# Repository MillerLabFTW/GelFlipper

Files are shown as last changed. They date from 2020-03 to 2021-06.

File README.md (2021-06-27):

# GelFlipper
#### Open-source gel flipper design for seeding endothelial cells
#### Miller Lab: Physiologic Systems Engineering and Advanced Materials
#### [millerlab.rice.edu](http://millerlab.rice.edu)
#### Project designed by Ian Kinstlinger; revised 04/2020

This repo provides fabrication files, Arduino code, and circuit schematics for our open-source gel flipping system for seeding endothelial cells into patterned vascular networks. See our [Nature Protocols paper](https://rdcu.be/clcY7) (specifically Box 1) for more info.

**Update 06/21:** We now provide blueprints and assembly instructions for our v2 flipper design, which is designed to replace the v1 hardware. Instead of interlocking gears, we use a single rotating block which holds multiple perfusion chambers. Up to 10 at a time are possible with our current design, which can be modified further. 

In our hands, this new version is more reliable because it eliminates occasional issues with the gears jamming during flipping. The main downside is that large gels cannot be flipped in large batches, and there is less flexibilty to swap in and out different gears.

**How to cite:** If you use this device for work in a publication, please cite this project as

Kinstlinger, I.S., Calderon, G.A., Royse, M.K. et al. Perfusion and endothelialization of engineered tissues with patterned vascular networks. Nat Protoc (2021). https://doi.org/10.1038/s41596-021-00533-1

**Questions:** Inquiries about this hardware, issues with assembly or operation, and feature requests can be directed to ian [dot] kinstlinger [at] gmail [dot] com.

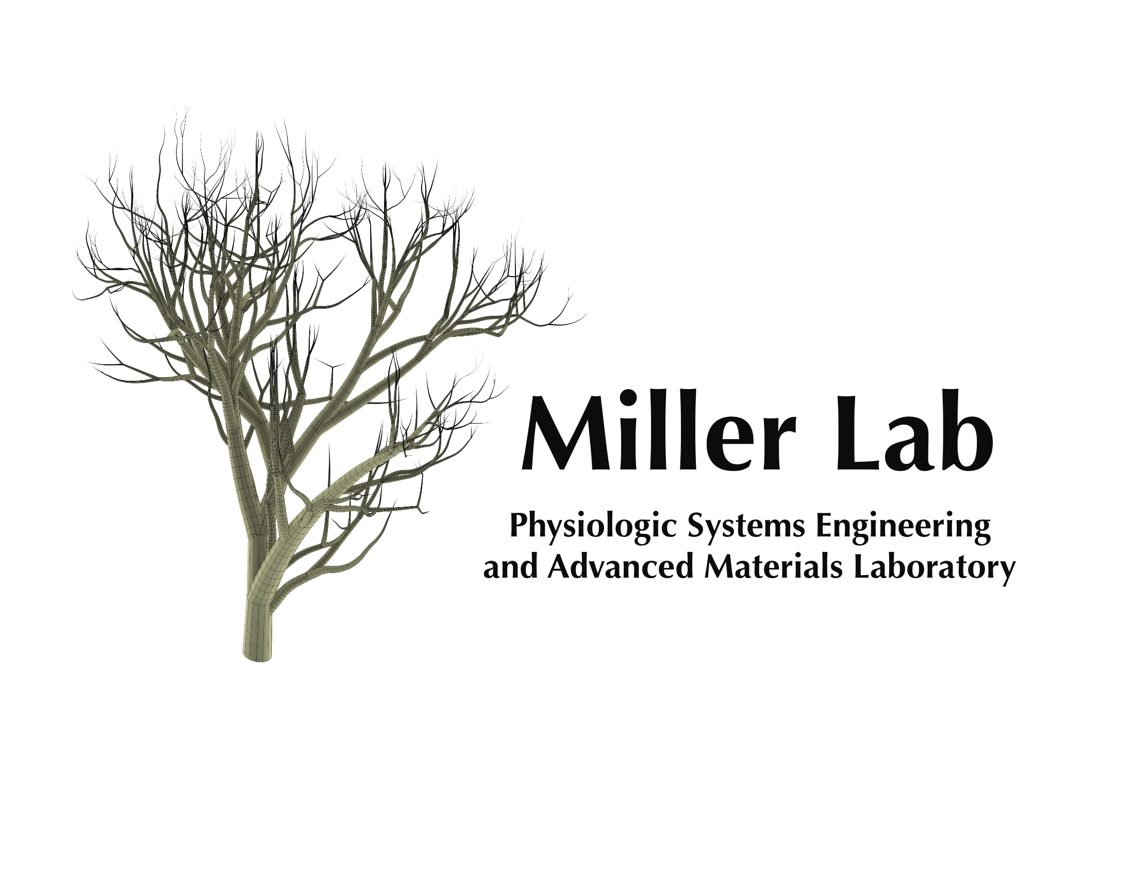
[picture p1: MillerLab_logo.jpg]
MillerLab logo


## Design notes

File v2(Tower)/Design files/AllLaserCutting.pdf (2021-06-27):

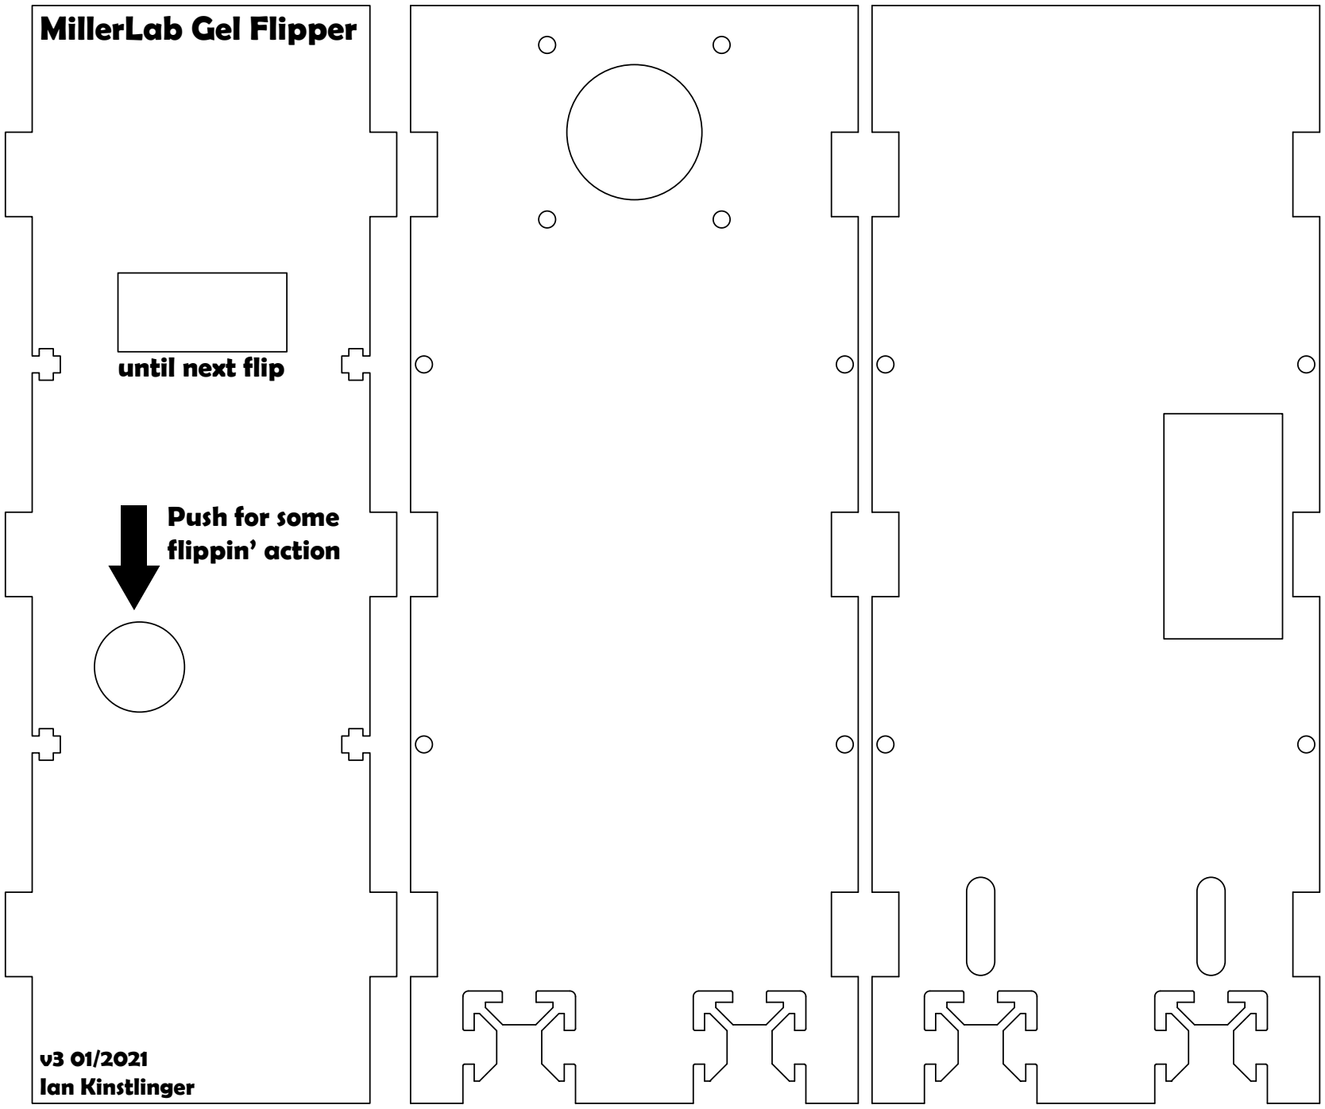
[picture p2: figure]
MillerLab Gel Flipper; until next flip; Push for some flippin’ action; v3 01/2021 Ian Kinstlinger

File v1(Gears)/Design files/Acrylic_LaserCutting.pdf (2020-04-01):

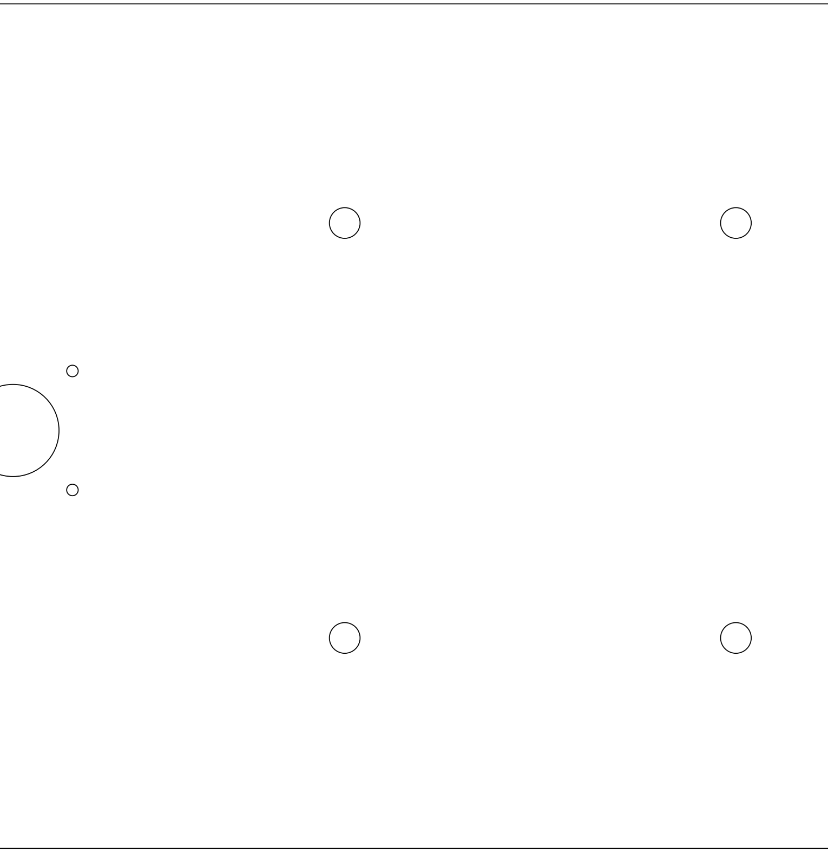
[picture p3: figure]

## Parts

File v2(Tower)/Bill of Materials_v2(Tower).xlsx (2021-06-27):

 | Perfusion chamber BOM
 | Part | Vendor | Part Number | Quantity | Notes
Electronics | Arduino Nano (or equivalent) | Amazon | Amazon link (https://www.amazon.com/Arduino-A000005-ARDUINO-Nano/dp/B0097AU5OU?ac_md=2-0-VW5kZXIgJDI1-ac_d_pm&cv_ct_cx=arduino+nano) | 1 | For all electronics items, there are many excellent vendors and suitable equivalent parts. This BOM is for a protoboard-based controller design, which requires permanently soldering the components to the board and to one another. An equivalent controller can be built on a breadboard, but we highly recommend the protoboard for making it permanent.
 | Protoboard | Amazon | Amazon link (https://www.amazon.com/Prototype-Universal-Protoboard-Soldering-Compatible/dp/B07W83VJGV?s=electronics) | 1
 | Pololu A4988 stepper motor driver | Pololu | 1182 | 1
 | NEMA 17 stepper motor | Adafruit | 324 | 1
 | LED pushbutton | Adafruit | 915 | 1
 | 2.1mm DC barrel jack for protoboard | Adafruit | 373 | 1
 | TM1637 4 digit 7-segment display | Amazon | Amazon link (https://www.amazon.com/OctagonStar-Digital-Display-Module-Arduino/dp/B01M16X6MB) | 1
 | Connector wires with 4-pin headers | Amazon | Amazon link (https://www.amazon.com/2-54mm-Breadboard-Testing-Jumper-Colorful/dp/B00O9Y3LGS) | 2
 | Breakaway headers | Adafruit | 400 | 1
 | Solid-core wire | Adafruit | 290 | 1
 | 12V DC power supply w/ barrel end | Adafruit | 352 | 1
Hardware | 3D printing filament (PLA or equivalent) | Ultimachine |  |  | Or your favorite filament vendor
 | Acrylic sheet, 12 x 24 x 0.375 in. (3/8" thick) | McMaster-Carr | 8589K61 | 1 | Many good vendors for acrylic sheets. We used 3/16" for this design
 | M3 x 10 screws | McMaster-Carr | 91292A113 | 1 pk of 100
 | M3 nuts | McMaster-Carr | 90591A250 | 1 pk of 100
 | M3 washers | McMaster-Carr | 93475A210 | 1 pk of 100
 | 20x20 mm aluminum T-slot extrusion | McMaster-Carr | 5537T911 | 2x ~12 inch pieces | Aluminum extrusions act as feet to stabilize the device; the exact length is not critical. If you have extrusion on hand, you can cut to length as needed with a hacksaw
 | Aluminum extrusion corner bracket | McMaster-Carr | 5537T81 | 2
 | Fastener nut for aluminum extrusion | McMaster-Carr | 5537T75 | 2
 | M5 x 12 screw | McMaster-Carr | 91274A127 | 1 (50 pack) | These nuts and bolts are to secure the aluminum extrusion -- the length of screw you need may depend on acrylic thickness and type of corner brackets used.
 | M5 nut | McMaster-Carr | 90592A095 | 1 (100 pack)
 | Fastener nut for aluminum extrusion | McMaster-Carr | 5537T75 | 2
 | (suggested) Acrylic glue; e.g. Weld-On SciGrip #4 | McMaster-Carr | 7517A1 | 1

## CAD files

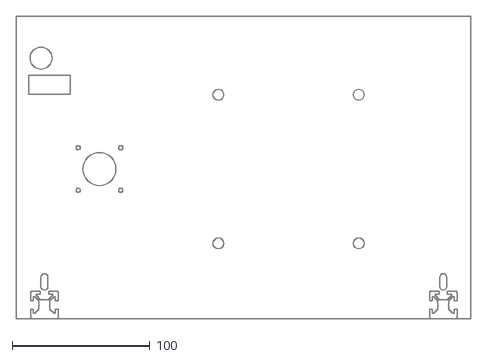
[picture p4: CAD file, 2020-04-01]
v1(Gears)/Design files/Acrylic_LaserCutting.dxf
330.5 x 220.0

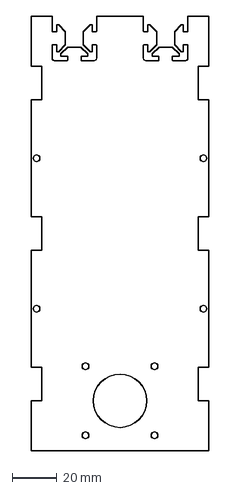
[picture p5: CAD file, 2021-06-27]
v2(Tower)/Design files/MotorSide.dxf
79.5 x 195.0 mm

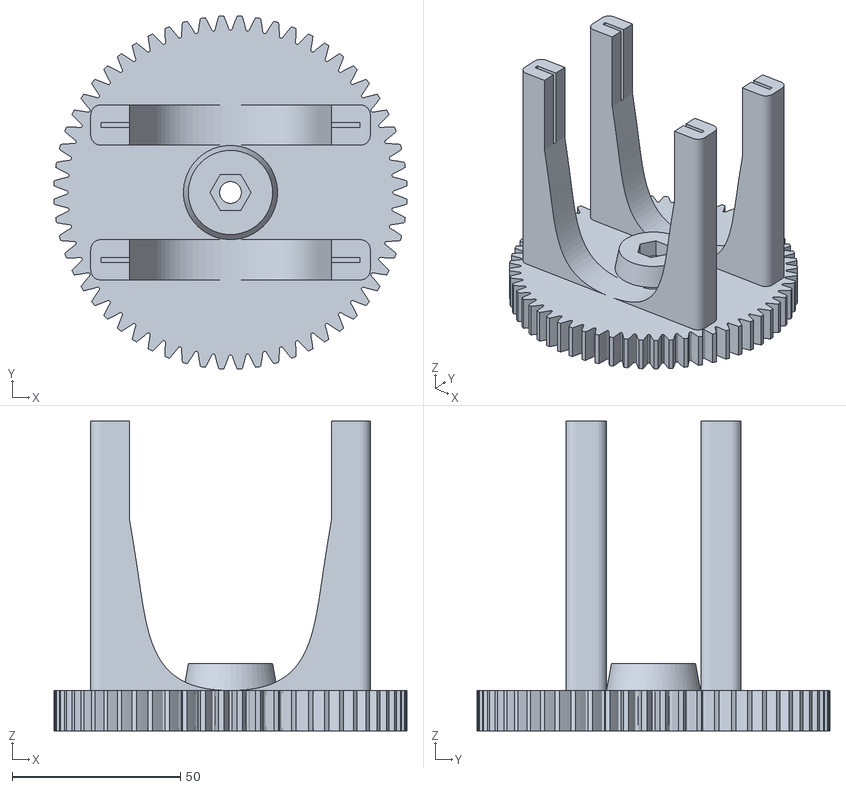
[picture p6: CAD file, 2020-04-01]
v1(Gears)/Design files/FlipGearv3.stl
104.8 x 104.8 x 92.0

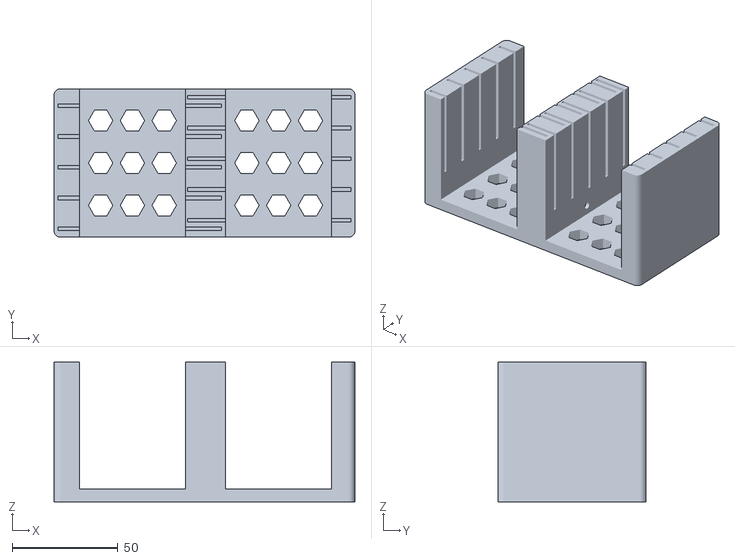
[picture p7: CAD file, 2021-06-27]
v2(Tower)/Design files/PerfChamberHolder.stl
142.0 x 70.0 x 66.0

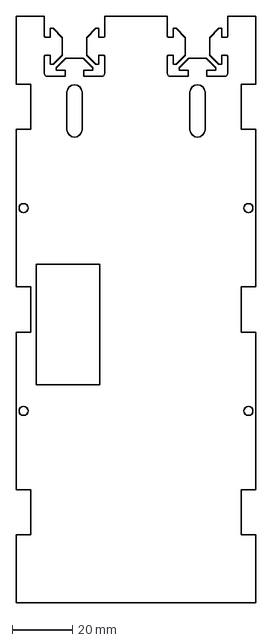
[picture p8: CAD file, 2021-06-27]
v2(Tower)/Design files/PlugSide.dxf
79.5 x 195.0 mm

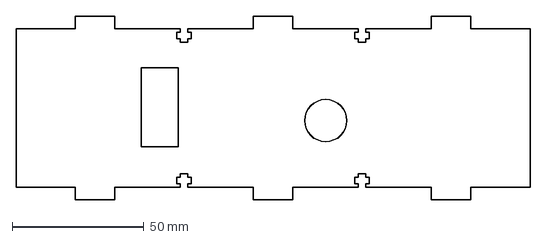
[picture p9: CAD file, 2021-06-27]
v2(Tower)/Design files/TimerSide.dxf
195.0 x 69.5 mm

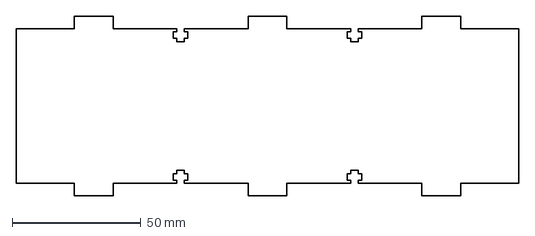
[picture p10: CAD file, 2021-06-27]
v2(Tower)/Design files/ControllerSide.dxf
195.0 x 69.5 mm

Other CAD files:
v1(Gears)/Design files/FlipGearMotorv3.stl
v2(Tower)/Design files/PerfChamberHolder.f3d

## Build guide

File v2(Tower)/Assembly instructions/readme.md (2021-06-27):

### Assembly instructions for gel flipper hardware -- tower version

### See BOM for parts list needed for this build

### 1. Fabricate laser-cut acrylic sheet and 3D print gears
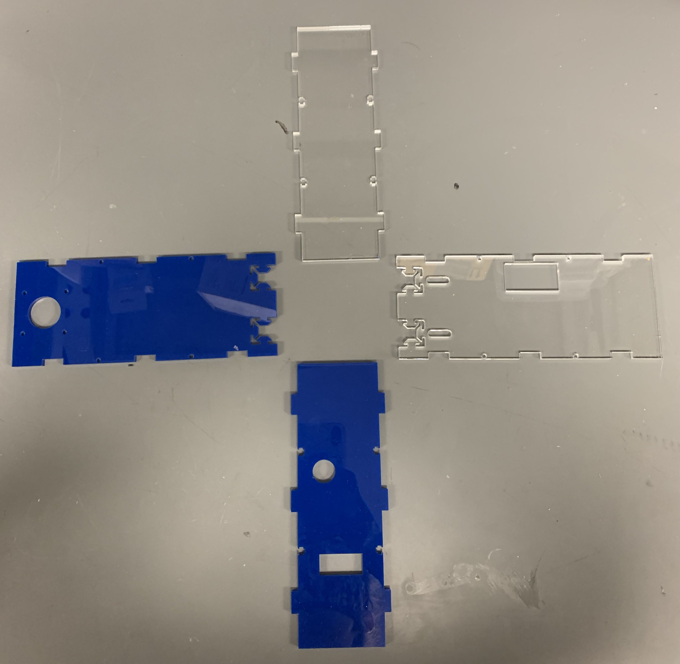
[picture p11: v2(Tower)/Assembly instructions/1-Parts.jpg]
Fabricate parts


Laser cutting: Adjust DXF file as needed. Interlocking tabs should change size if you use acrylic of thickness other than 3/16". Text is added in the Illustrator and PDF files. Fun color and customizations are encouraged!
3D printing: Print the chamber-holding piece which slides onto the motor shaft (not shown here). 

### 2. Assemble first two walls
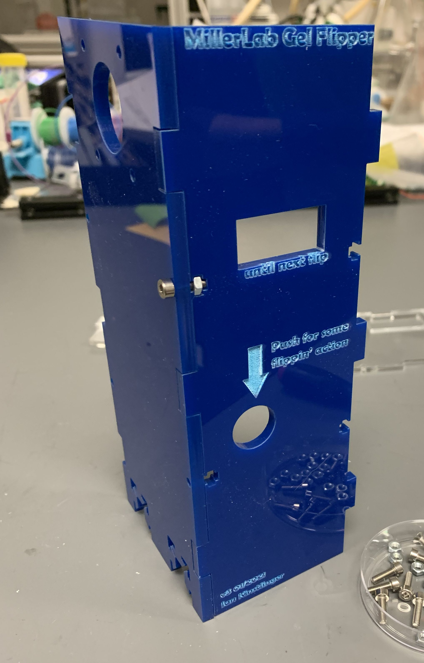
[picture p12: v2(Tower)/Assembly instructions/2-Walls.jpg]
Build walls


Use M3-10mm bolts and M3 nuts to secure the motor-side wall to the button-side wall. Nuts slide into the traps from the side. Carefully tighten until the pieces don't wiggle, but don't overtighten or the acrylic can crack.

### 3. Attach NEMA 17 motor
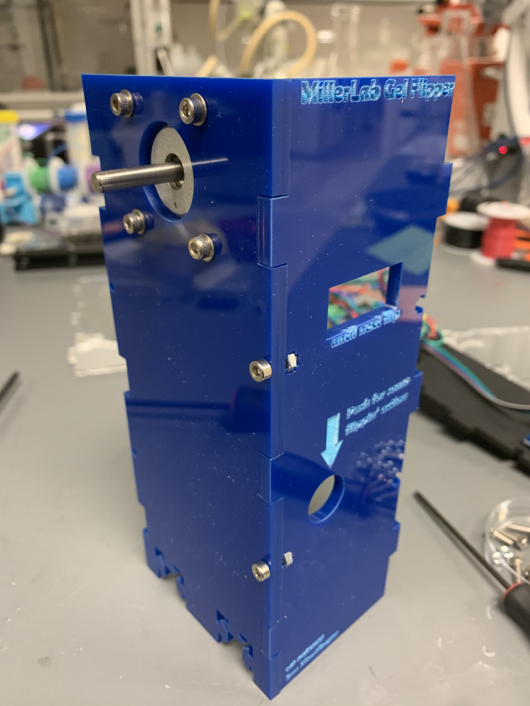
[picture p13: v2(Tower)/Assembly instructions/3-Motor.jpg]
Attach motor


Use M3 hex bolts and washers.

### 4. Mount button and time display
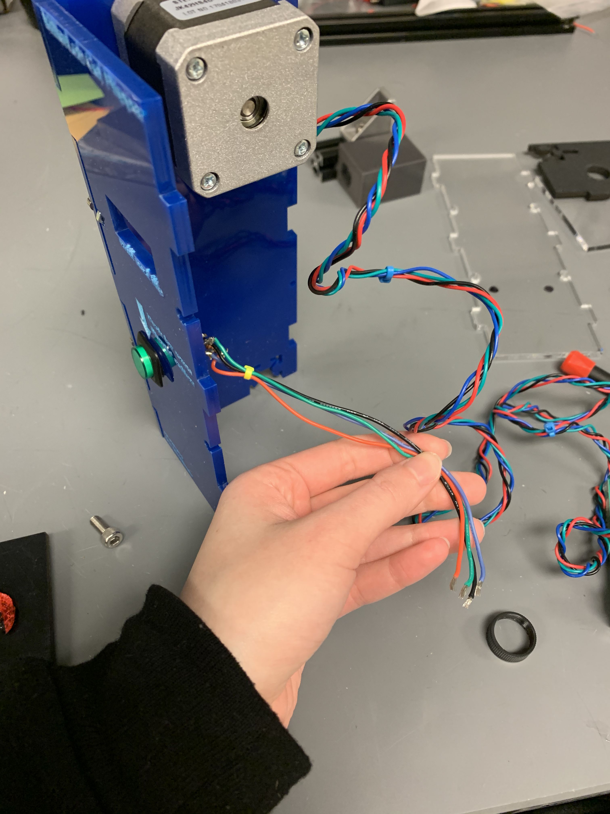
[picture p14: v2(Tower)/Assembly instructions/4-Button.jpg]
Mount motor gear


Install the 7 segment display and start/stop button into the laser-cut slots. If the display is not snug against the acrylic, it can be hot glued or taped from the back.

### 5. Mount controller onto acrylic wall
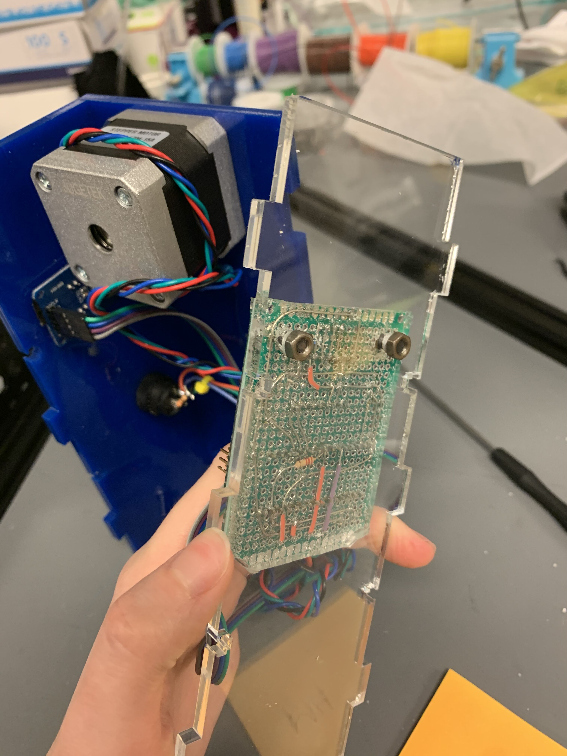
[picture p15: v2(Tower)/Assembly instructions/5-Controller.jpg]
Mount controller


Use nuts and bolts to attach the Arduino controller to the acrylic piece shown. Here, we drilled 4mm holes in the acrylic and the protoboard. You can also add these holes to the original laser cutting file. It doesn't matter what diameter bolts are used, but we used M4 here. Note that we also encased the controller circuit in PDMS (Sylgard 184) to protect it from degradation in the incubator.

### 6. Join controller wall with other walls
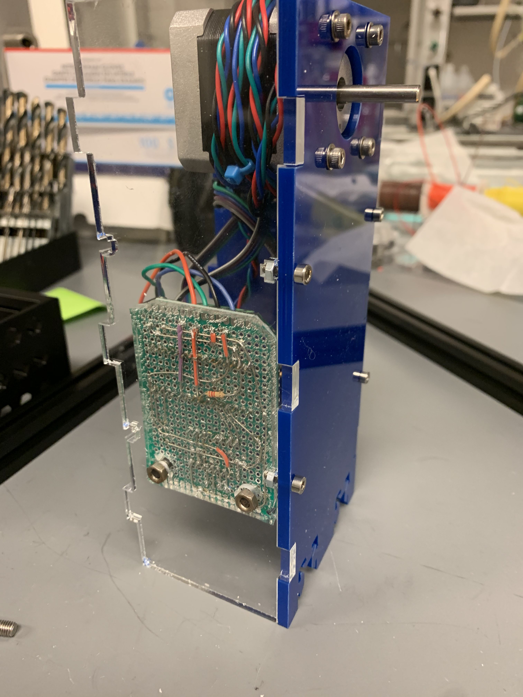
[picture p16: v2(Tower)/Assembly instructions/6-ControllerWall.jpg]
Join walls


Use more M3-10mm bolts and nuts to add the third wall to the first two. At this stage, we suggest using acrylic glue to semi-permanently hold together these 3 walls. Use caution when handling the glue; wear gloves and safety glasses and work in a well-ventilated workspace.

At this point, if not already connected, plug the start button and timer display into the controller. 

### 7. Mount aluminum T-slot legs onto final wall
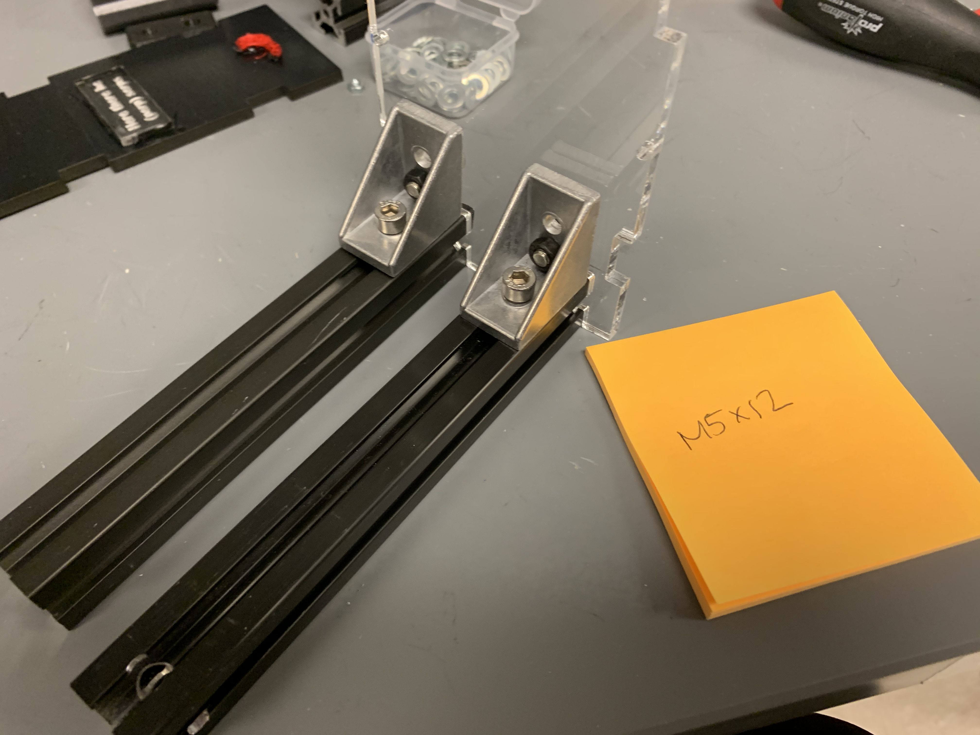
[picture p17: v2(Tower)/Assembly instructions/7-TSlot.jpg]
Mount T-slot


We use T-Slot extrusion as a stable base for the flipper so that when gels are flipped, their added weight doesn't topple the tower. It can be cut to size with a hacksaw, and the exact length is not critical as long as the tower is stable.

Here we use M5 nuts and brackets to secure the T-slot; other mounting hardware is possible too.

### 8. Assemble final  wall
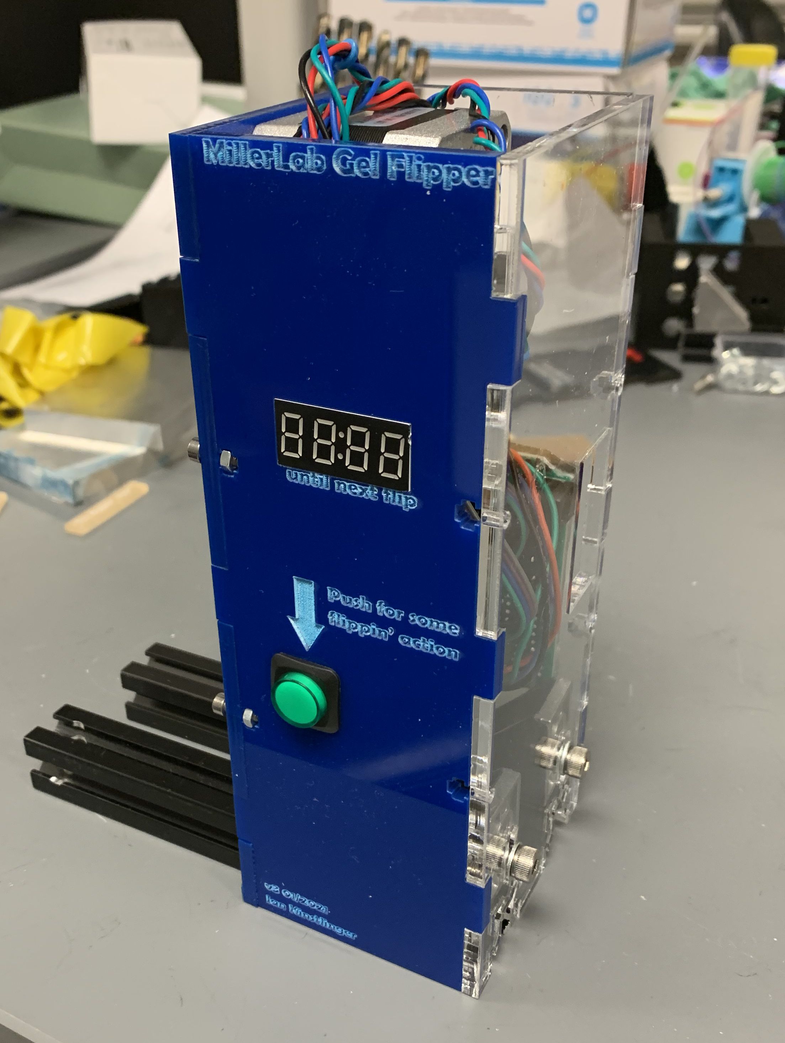
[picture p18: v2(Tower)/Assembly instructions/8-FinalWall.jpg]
Final wall


Feed the free end of the aluminum extrusion through the slots in the motor-side wall until the final wall slots into place. Use M3-10mm bolts to secure.

### 9. Add chamber holder
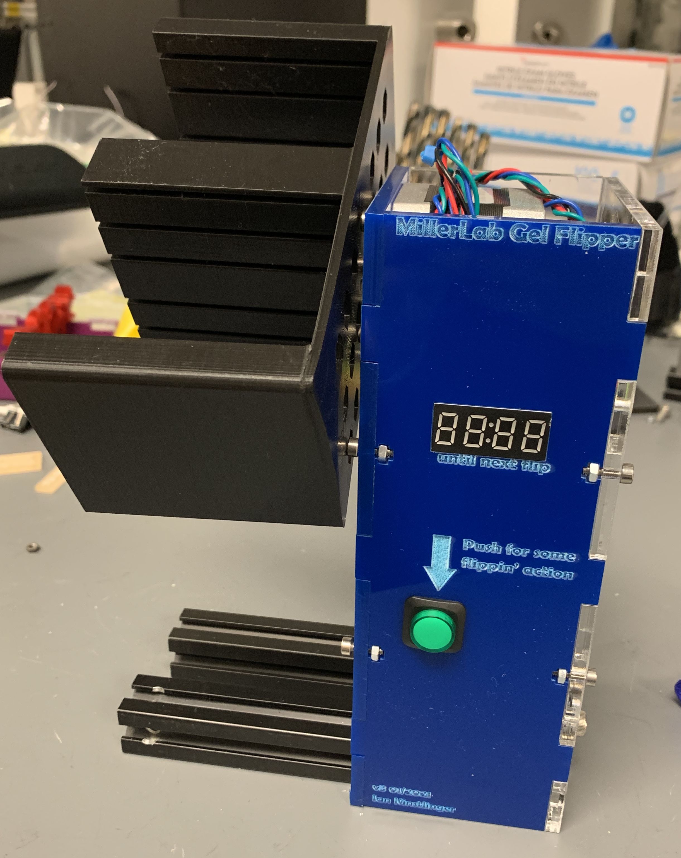
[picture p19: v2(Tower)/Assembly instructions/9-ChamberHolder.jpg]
Chamber holder


Press-fit the 3D printed gel perfusion chamber holder onto the shaft of the motor. If it does not slide on, or is too tight, you may need to adjust the size of the shaft hole in Fusion, then re-print. 

At this point, the flipper is fully assembled. Flash firmware onto the Arduino and give it a spin!

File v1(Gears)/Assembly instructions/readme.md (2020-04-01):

### Assembly instructions for gel flipper hardware 
### See BOM for parts list needed for this build

### 1. Fabricate laser-cut acrylic sheet and 3D print gears
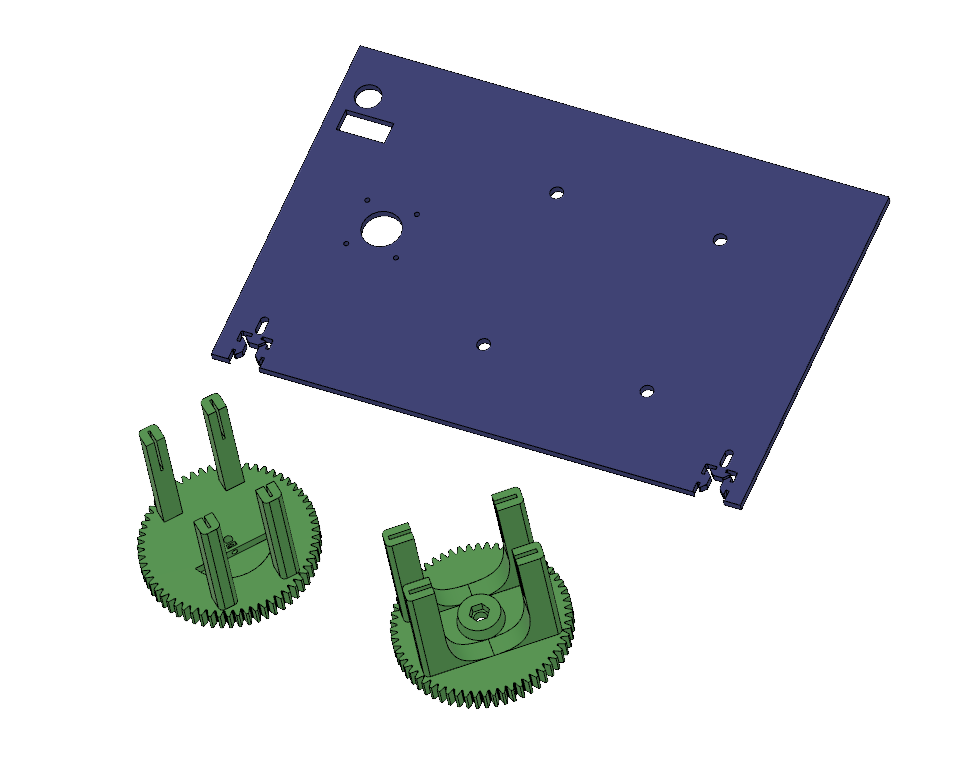
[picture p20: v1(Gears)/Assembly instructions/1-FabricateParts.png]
Fabricate parts


Laser cutting: Adjust DXF file as needed for a larger or smaller flipper design. Gears should be 102 mm apart, center-to-center. Fun customizations are highly encouraged!
3D printing: Print one motor gear (mounts to a NEMA 17 shaft) and 4x (or as many as needed for your altered design) free gears which spin on bearings. Custom gear designs can help you fit more gels on at a time, use a gear radius (including teeth) of 60 mm.

### 2. Attach NEMA 17 motor
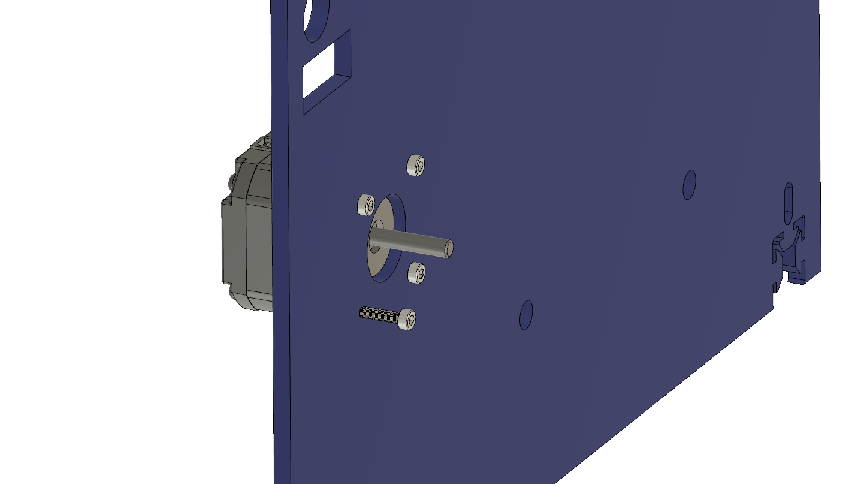
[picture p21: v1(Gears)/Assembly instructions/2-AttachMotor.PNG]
Attach motor


Use standard M3 hex bolts

### 3. Mount motor gear
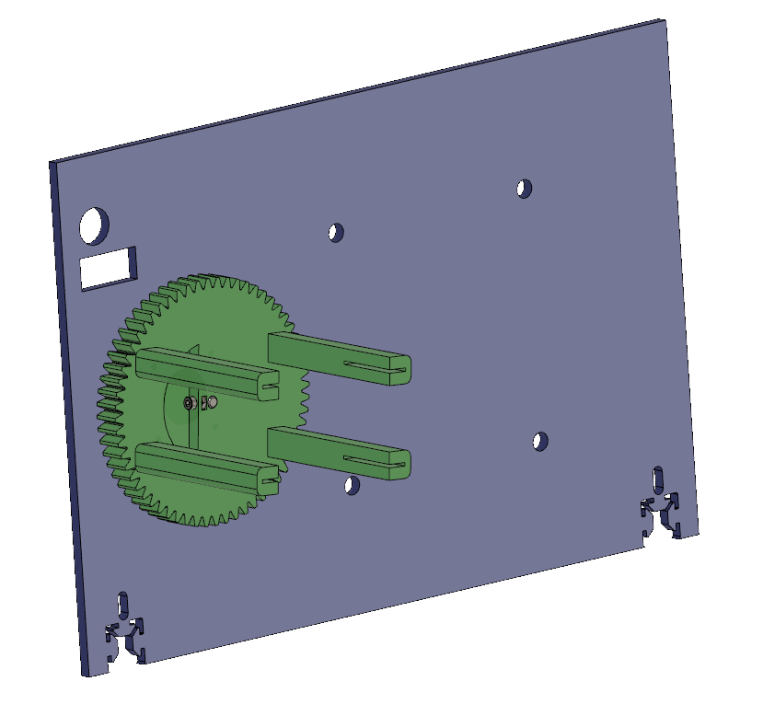
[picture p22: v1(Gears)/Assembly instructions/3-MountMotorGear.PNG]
Mount motor gear


Depending on the tolerance of your printer, the gear may sit tightly on the shaft, or may need to be secured. Use an M3x6 set screw and M3 nut to lock it in place

### 4. Mount free gear
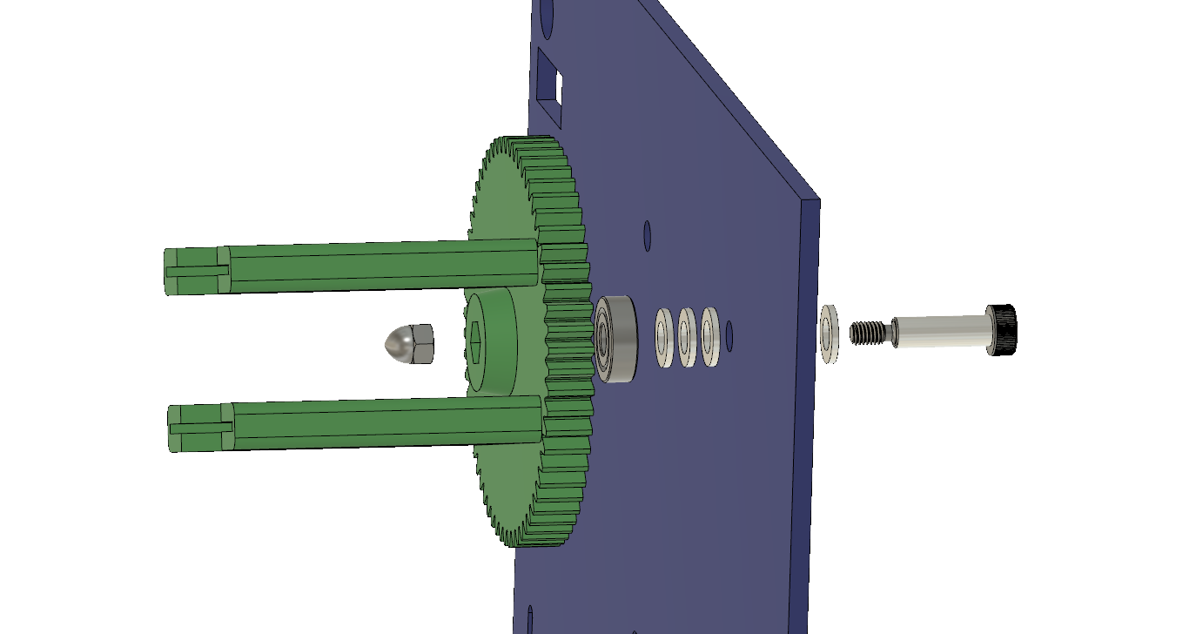
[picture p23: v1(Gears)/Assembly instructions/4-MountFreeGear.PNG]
Mount free gear


First, mount the 608z bearing into the recess in the back face of the gear, making sure the surfaces are flush. Depending how tight the fit is, you may need to tap gently with a mallet. Then slide the shoulder screw through as many washers as needed, through the bearing, and secure with the cap nut. Don't overtighten, and make sure that the bearing spins smoothly. 

### 5. Mount remaining free gears
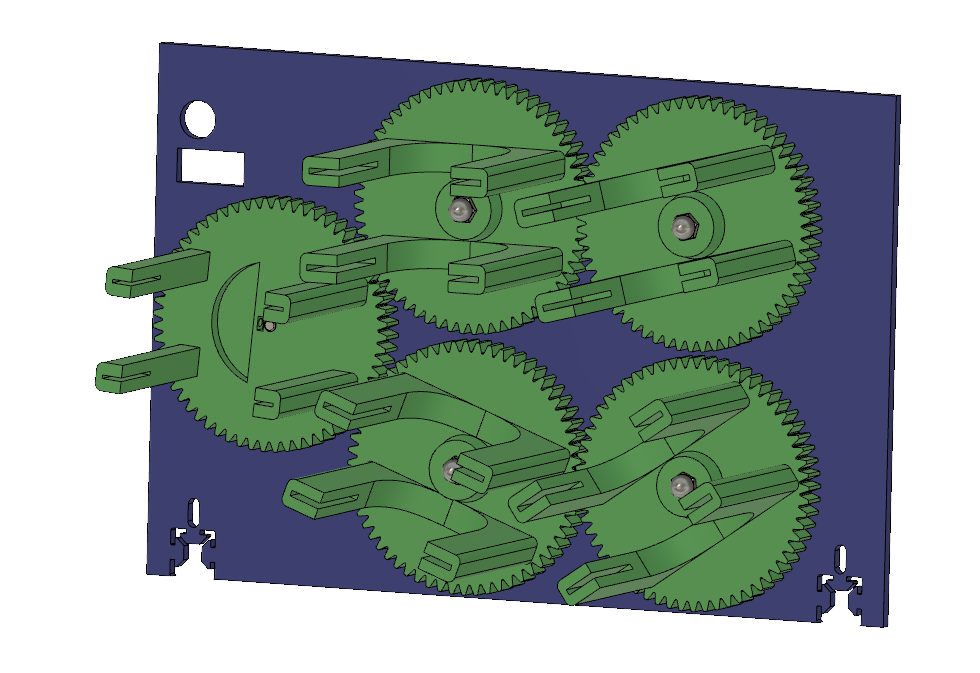
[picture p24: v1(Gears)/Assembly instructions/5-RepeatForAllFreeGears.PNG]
Repeat


Repeat step 4 for remaining free gears. Carefully line up the teeth of the gears and make sure they all spin smoothly when spun by hand. If they don't spin smoothly, check individual gears and make sure the bearings are aligned with the gears. 

### 6. Add feet for stability
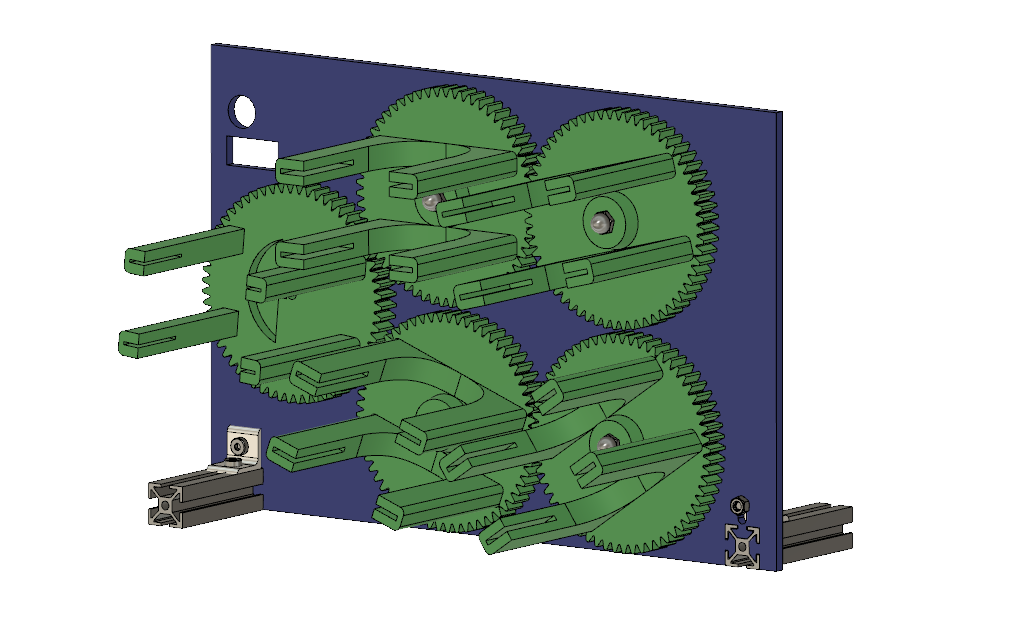
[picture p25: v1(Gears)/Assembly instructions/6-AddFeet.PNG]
Add feet


You can design feet in other ways, but this is quick and easy if you have some spare aluminum extrusion. Use M5 screws and corner brackets to secure, or adjust the acrylic lasercutting pattern for your needs.

### 7. Mount electronics
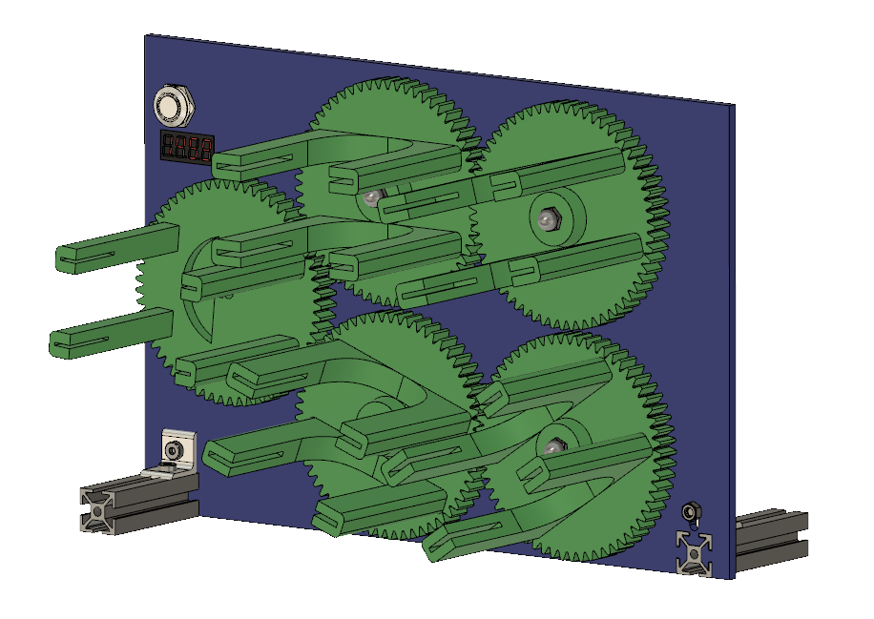
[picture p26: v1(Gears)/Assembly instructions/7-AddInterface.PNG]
AddInterface


The push buttons from Adafruit have a nice collar design for mounting on a panel. The 4 digit display may be screwed in, but we used some hot glue. For the main controller, we drilled some extra holes in the acrylic and mounted with aluminum spacers, see below.

## Finished product:

### Front view: 
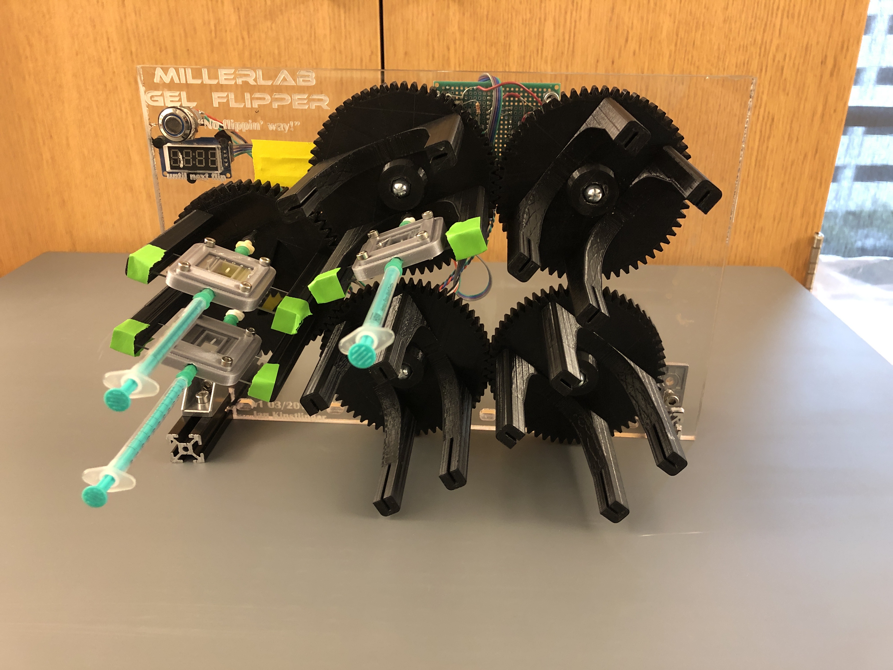
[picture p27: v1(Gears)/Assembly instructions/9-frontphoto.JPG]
Front view


### Back view:
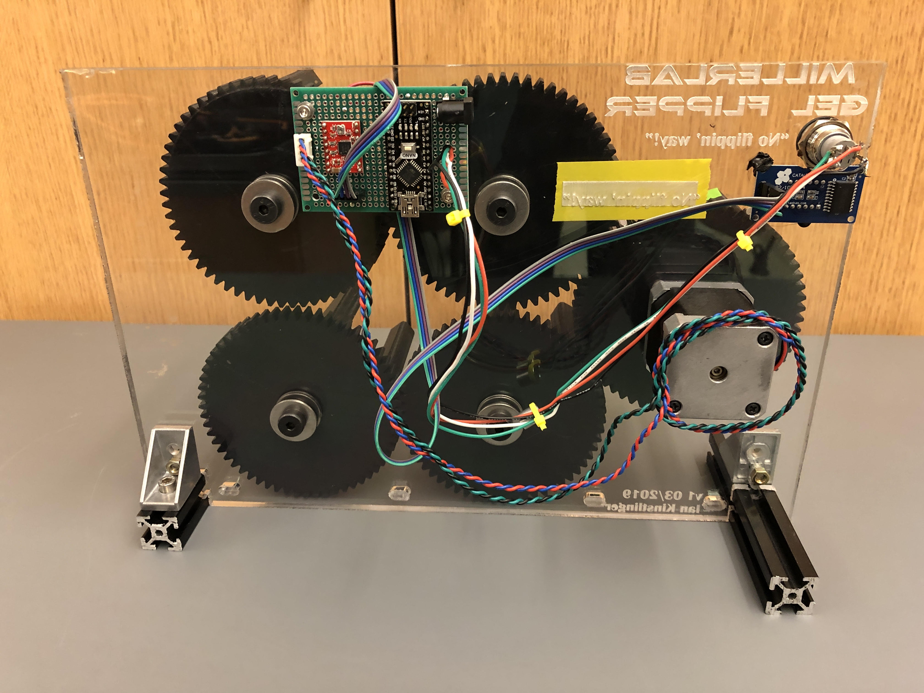
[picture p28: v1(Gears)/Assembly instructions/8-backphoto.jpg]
Back view


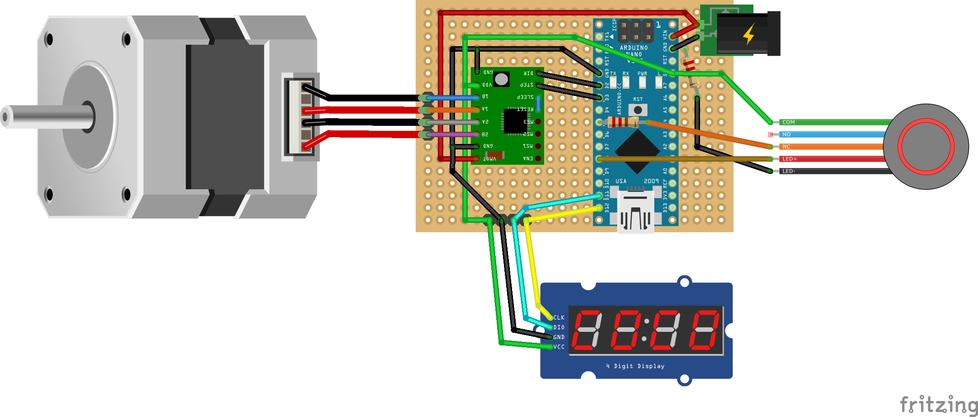
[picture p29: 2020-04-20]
Firmware and electronics/v1_wiringDiagram.png

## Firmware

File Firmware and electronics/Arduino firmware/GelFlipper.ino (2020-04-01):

#include <AccelStepper.h>
#include "SevenSegmentTM1637.h"
#include "SevenSegmentExtended.h"

/* initialize global TM1637 Display object
*  The constructor takes two arguments, the number of the clock pin and the digital output pin:
* SevenSegmentTM1637(byte pinCLK, byte pinDIO);
*/
const byte PIN_CLK = 11;   // define CLK pin (any digital pin)
const byte PIN_DIO = 12;   // define DIO pin (any digital pin)
SevenSegmentExtended      display(PIN_CLK, PIN_DIO);
AccelStepper motor(2,2,3);

const int buttonDetect(5);
const int buttonLED(8);

int buttonState = 0;
int flipping = 0;
byte timePerFlip = 15; //mins

// run setup code
void setup() {
  Serial.begin(9600);         // initializes the Serial connection @ 9600 baud
  display.begin();            // initializes the display
  display.setBacklight(100);  // set the brightness to 100 %
  delay(1000);                // wait 1000 ms

  pinMode(buttonDetect,INPUT);
  pinMode(buttonLED, OUTPUT);
  

  motor.setMaxSpeed(1000.0);
  motor.setAcceleration(400.0);

  //digitalWrite(buttonLED, HIGH);


};

// run loop (forever)

void loop() {

      while(flipping == 0){
        display.clear();
        display.print("OFF");

        digitalWrite(buttonLED, HIGH);
        delay(1000);
        buttonState = digitalRead(buttonDetect);
        digitalWrite(buttonLED, LOW);
        delay(1000);

        if(buttonState == 0){ //start flipping
          flipping = 1;

          digitalWrite(buttonLED, HIGH);

          display.print("LETS");
          delay(1000);
          display.print("FLIP");
          delay(1000);
          display.clear();
          delay(1000);


          break;
        }
        
      }

      byte minsLeft = timePerFlip;
      byte secsLeft = 60;

      
    
      for ( ; minsLeft > 0 ; minsLeft--){
        for(; secsLeft > 0 ; secsLeft--){

          buttonState = digitalRead(buttonDetect);
          Serial.println(buttonState);

          if(buttonState == 0){ //button pressed
            flipping = 0;
            break;
            
          }
          
          display.printTime(minsLeft-1, secsLeft-1, true);
          delay(1000); //1000 ms = 1 sec
        
       }
        secsLeft = 60;
        if(buttonState == 0){
          flipping = 0;
          break;
        }
      }

      if(flipping == 1){
        display.print("FLIP");
        motor.runToNewPosition(405*8); //.5 for perpserp
        motor.setCurrentPosition(0);
        //motor.runToNewPosition(405*8);
      }


  
};

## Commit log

2020-04-01 Add photos and design files
    [Acrylic_LaserCutting.dxf, FlipGearMotorv3.stl, FlipGearv3.stl]
2020-04-01 Start drafting assembly instructions
2020-04-01 More assembly instructions
2020-04-01 Arduino files
2020-04-09 Add BOM
    [Bill of Materials.xlsx]
2020-04-20 Add wiring diagram
2021-06-27 Add v2 flipper
    [Acrylic_LaserCutting.dxf, Bill of Materials_v1(Gears).xlsx, Bill of Materials_v2(Tower).xlsx, ControllerSide.dxf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]
